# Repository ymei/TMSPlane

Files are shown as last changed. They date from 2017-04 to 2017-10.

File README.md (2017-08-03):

# Topmetal-S sensor tiled plane

## PCB

We use KiCad and python script to generate schematic, footprint, and PCB layout with minimal manual intervention.

### Procedure:
#### Schematic
1. Draw a Topmetal-S schematic symbol and save in a SCH library ```TMSch.lib```.  ```TMSch.lib``` is symlink-ed to every project.  When modifying the library, open the original ```.lib''' file directly instead of opening the symlinks.
2. run ```GenSch.py``` to generate desired schematic for the TMS array with correct net connectivity.  Here we save the generated file as ```array.sch```, which is a 2nd-level hierarchical schematic under ```Phi10cmBonding.sch```.
3. Open ```Phi10cmBonding.sch``` and generate a netlist.
#### PCB
1. Run ```KiPcbFp.py``` to generate a footprint ```TMS1mm.kicad_mod``` and save it under ```TMPcb.pretty``` which is a footprint library.  One may need to modify ```~/.config/kicad/fp-lib-table``` in order for KiCad to find the library: ```(lib (name Topmetal)(type KiCad)(uri ${KIPRJMOD}/TMPcb.pretty)(options "")(descr "Topmetal bonding footprints"))```.  An alternative is to save a local ```fp-lib-table``` file in the project directory.
2. Use pcbnew manually to setup a PCB `template' with appropriate layer structure, via and track classes etc.  Here we call the template ```template.kicad_pcb```.
3. Draw trace connections within a single footprint using a copy of the template PCB.  Save the single chip SCH and PCB as ```TMS1mm1chip.{sch,kicad_pcb}```.  It is preferable to place TMS1mm module's center at the very center in the unit cell.  It will be used as a reference (local origin).
4. Make a copy of the template PCB and load the netlist into it.  This step will bring all footprints into the PCB.
5. Run ```GenPcb.py``` which references the netlist-loaded PCB and ```TMS1mm1chip.pcb```, and generates the correctly laid out array.
6. **Remember to press `b' in pcbnew** to (re-)fill zones.

## Software
### KiCad

Pull source from https://github.com/KiCad/kicad-source-mirror and compile.

### KiCadScript in Hardware/PCB/KiCadScript/

#### Run scripts in Pcbnew's python shell:
```
import os, sys, runpy
scriptPath = os.environ['KIPRJMOD'] + "/../KiCadScript"
sys.path.append(scriptPath)
sys.argv = ['', '-h']
fileGlobals = runpy.run_path(scriptPath + "/GenSch2ExDAC.py", run_name="__main__")
```

#### Compile C source code to be used in python
```sh
cd KiAuto/hexlib/
python setup.py build
cd build
ln -s lib.freebsd-11.0-STABLE-amd64-2.7/hexlib.so .
```

### KiCad schematic sheets and netnames
KiCad schematic sheets are organized hierarchically.  Sheet paths are named as ```/58F9164E/58F91649``` with the numbers being timestamps in hex format.  Netnames local to a sheet start with a leading ```/```.  Global netnames do not have leading ```/```.

# PCB design and manufacturing

## Manufacturer capabilities

[Sunstone capabilities](http://www.sunstone.com/pcb-manufacturing-capabilities/detailed-capabilities)

|                     | Sunstone preferred | Sunstone capable |
| ------------------- |:------------------ |:---------------- |
| minimum drill size  | 0.008"             | 0.005"           |
| minimum trace width | 0.004" 1 oz Cu     | 0.003"           |
| trace clearance     | 0.004" 1 oz Cu     | 0.003"           |
| through-hole pad dia | 0.018" larger than finished hole dia | 0.016" larger |

Finished hole dia = drill dia - 4mil

### Typical board thickness in inch
```
0.062, 0.093, 0.125, 0.0886(14-layer), 0.0756 (16-layer)
```
1oz copper thickness is 34um (1.34mil)

### Typical drill sizes diameter in inch
```
0.008, 0.014, 0.020, 0.025, 0.029, 0.033, 0.035, 0.040, 0.043, 0.046, 0.052, 0.061,
0.067, 0.079, 0.088, 0.093, 0.100, 0.110, 0.125, 0.141, 0.150, 0.167, 0.192, 0.251
```
For boards thicker than 100mil, usually drill size cannot be smaller than board thickness / 10 (aspect ratio).

### Via
A recommendation: make the drill size diameter the same as the width of the trace, and the pad size roughly twice the diameter.

### Impedance
width/clearance 6mil/6mil and 4mil/4mil on surface layers, 4mil/7mil and 4mil/10mil inner layers are commonly used for Zo=50Ohm, Zdiff=100Ohm.

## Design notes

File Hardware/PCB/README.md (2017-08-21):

# TMS1mmX19 Carrier board (with TE0741 FPGA module)

1. Schematic done in KiCad, .asc netlist generated then imported into Mentor PADS for layout.  Remember to delete all **Nets** and modified/unwanted components in PADS before importing .asc.

## Features
1. TMS array power is logic (firmware/software) controlled via LDO EN pins.  Due to power-rail sharing, the relevant bias voltages and serial IO are also controlled by the switches.
2. All LDO design, no DC/DC.  For maximal efficiency, supply 4V power.  Maximum 5V allowed.
3. Serial IO, SDI, SDO, SCK, are multiplexed to drive one column (chain) at a time.  SDI and SCK have `high' as their idle states.

## Power requirement

### LTC2325-16 ADC
1. DVDD2V5 for OVdd: 31.5mA max
2. AVDD3V3 for Vdd : 44.5mA max

5 ADCs total, DVDD2V5: 157.5mA, AVDD3V3: 222.5mA

### LMK00105 for distributing CNVn to ADCs
1. DVDD2V5: 48mA

### 100MHz clock + CDCLVD1208 Clock distribution to ADCs
1. DVDD2V5: 25 + 75mA = 100mA

### 25MHz clock + CDCLVD1208 Clock distribution to SDMs
1. DVDD2V5: 90 + 75mA = 165mA

### ADR3412 + OPA350 for LVDS_VREF
1. DVDD2V5: 1 + 8.5mA = 10mA

DVDD2V5 requires total 545.5mA

# TMS1mmX19 19-chip array bonding board
## Signals and layers
### 16-layer stack-up, for 19-chip array TMS1mmX19.  Thickness 75.6mil, 1oz copper
1  F.Cu    Top copper layer
2  In1.Cu  AGND
3  In2.Cu  GND_NMOSI, DAC_BufferX2_VREF
4  In3.Cu  Gring, Ref3
5  In4.Cu  Ref2
6  In5.Cu  SDM_VDD_Shield, GND_VREF
7  In6.Cu  LVDS_VREF, Ref1
8  In7.Cu  AVDD
9  In8.Cu  AGND fill + RESET (as traces), SDM_testIN (as traces)
10 In9.Cu  DGND fill + slow digital signals: SDI, SDO, SCK
11 In10.Cu SDM_OUT1
12 In11.Cu DGND
13 In12.Cu CLK_P
14 In13.Cu CLK_N, SDM_OUT2
15 In14.Cu DVDD
16 B.Cu    Bottom copper layer

### 3.0mm-thick board produced by Edadoc
```
    Thickness(mil),   material,  DK
F.Cu 0.5oz+plating
    2.73 PP(1080 RC64)           3.81
In1.Cu  1oz
    5.12 CORE                    3.99
In2.Cu  1oz
    6.84 PP(1080 RC64+2116 RC57) 3.91
In3.Cu  1oz
    3.94 CORE                    4.12
In4.Cu  1oz
    5.04 PP(1080 RC64+1080 RC64) 3.81
In5.Cu  1oz
   18.11 CORE                    4.16
In6.Cu  1oz
    3.55 PP(106 RC76+106 RC76)   3.55
In7.Cu  1oz
    5.91 CORE                    4.25
In8.Cu  1oz
    4.01 PP(106 RC76+106 RC76)   3.55
In9.Cu  1oz
   18.11 CORE                    4.16
In10.Cu 1oz
    4.81 PP(1080 RC64+1080 RC64) 3.81
In11.Cu 1oz
    3.94 CORE                    4.12
In12.Cu 1oz
    6.30 PP(2116 RC57+1080 RC64) 3.91
In13.Cu 1oz
    5.12 CORE                    3.99
In14.Cu 1oz
    2.88 PP(1080 RC64)           3.81
B.Cu 0.5oz+plating
```

## FABRICATION NOTES
**All notes are applicable unless otherwise specified**

1. Materials: Green clad FR-4/Epoxy glass or equivalent.  Dielectric constant 4.2+/-0.2.  See cross-section drawing for board thickness, copper weight and layer structures.  RoHS compliant.
2. Components on top (front) and bottom (back) layers.
3. Minimum signal trace width/spacing: 4/4 mils.
4. Drilling.
  1. Minimum drill size is 8mil.
  2. All plated holes are to be plated through and with minimum copper thickness of 1mil.
  3. Drill sizes specified are actual drill sizes.  Finished hole sizes are expected to be 3~4mil smaller than the drill size.
  4. All PTH are to be within +/-3mil from true positions, NPTH to be within +/-2mil.
  5. See hole size table in the supplied NC drill file.
5. Layer-to-layer (pattern-to-pattern) registration (alignment) shall be within +/-5mil.
6. Soldermask: both sides of board, Liquid Photo Imageable, soldermask over bare copper (SMOBC), green.
7. Warpage and twist to meet IPC class II.  Shall not exceed 7mil per inch measured at any location or direction on the board.
8. Silkscreen shall use white non-conductive epoxy or equivalent.  Ink is NOT allowed on exposed plated area.
9. Finish.
  1. Edges to be free of loose silver and rough edge.
  2. Finished board shall not have nicks, scratches, voids, exposed copper, poor plating or mis-drilled holes.
  3. Trace width tolerance = +/-1mil of specified trace width.
  4. ENIG (Electroless nickel immersion gold) finish over copper.
10. Delivered boards shall be free of dirt, oil, finger prints and other contaminants.
11. Remove non-functional pad on all inner layers.
12. Manufacture's UL marking, flammability rating, logo and data code to be placed in silkscreen on bottom side of the board.
13. Impedance control
  1. All 19mil-wide traces on outer layers shall be 50Ohm single-ended +/-10%
  2. All 6mil/6mil width/spacing traces, including 4mil/4mil on outer layers and 4mil/7mil on inner layers shall be 100Ohm differential +/-10%

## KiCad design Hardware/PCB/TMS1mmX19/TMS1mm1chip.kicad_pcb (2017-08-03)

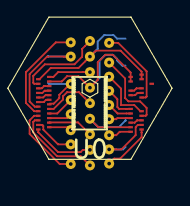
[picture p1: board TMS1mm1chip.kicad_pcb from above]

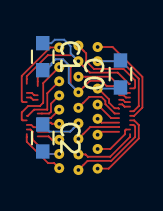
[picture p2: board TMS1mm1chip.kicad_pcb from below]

Board: 16 copper layers, 4 parts (3 on the bottom side), 12 nets.

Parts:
C0, C1, C2: 1u; C_0603
U0: TMS1mmAout1or2

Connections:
/AGND: C1.2, C2.2, U0.3, U0.28, U0.47, U0.49
/AVDD: C1.1, C2.1, U0.2, U0.27, U0.48, U0.50
/CSA_VBIASN_{}: U0.41, U0.42
/CSA_VBIASP_{}: U0.43, U0.44
/CSA_VDIS_{}: U0.7, U0.8
/CSA_VREF_{}: U0.5, U0.6
/DGND: C0.2, U0.14
/DVDD: C0.1, U0.13
/SDM_BIAS_{}: U0.29, U0.30
/SDO_{}: U0.24, U0.25
/VCASN_{}: U0.9, U0.10
/VCASP_{}: U0.11, U0.12

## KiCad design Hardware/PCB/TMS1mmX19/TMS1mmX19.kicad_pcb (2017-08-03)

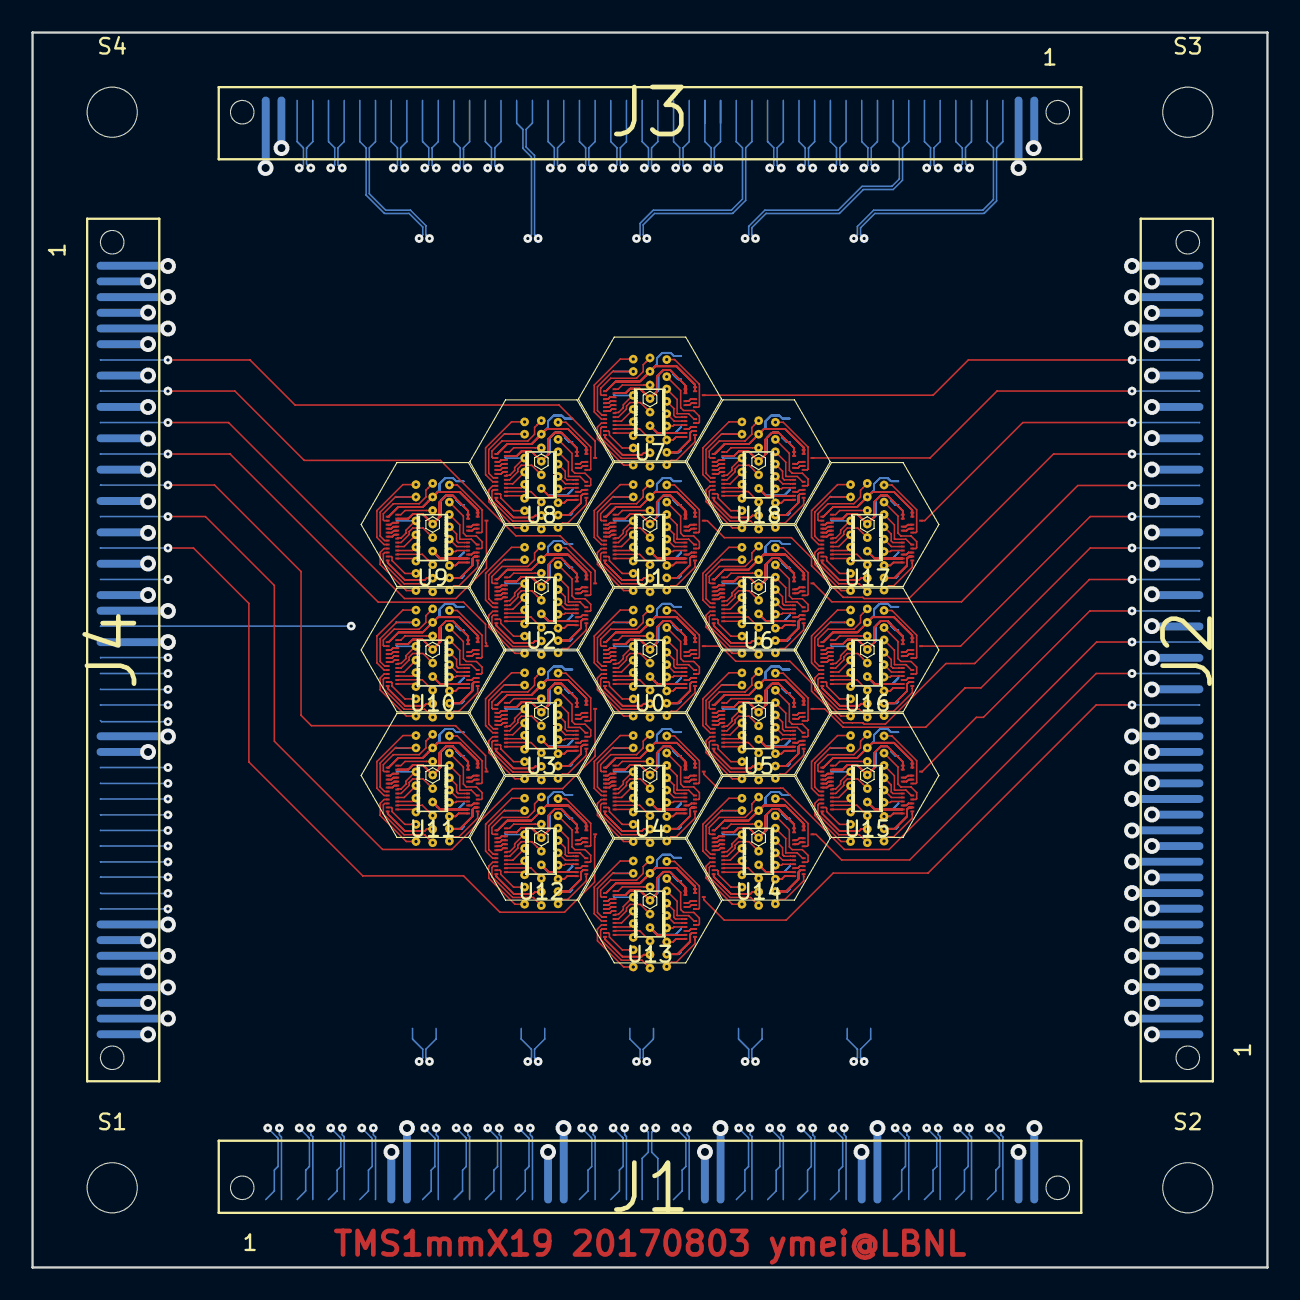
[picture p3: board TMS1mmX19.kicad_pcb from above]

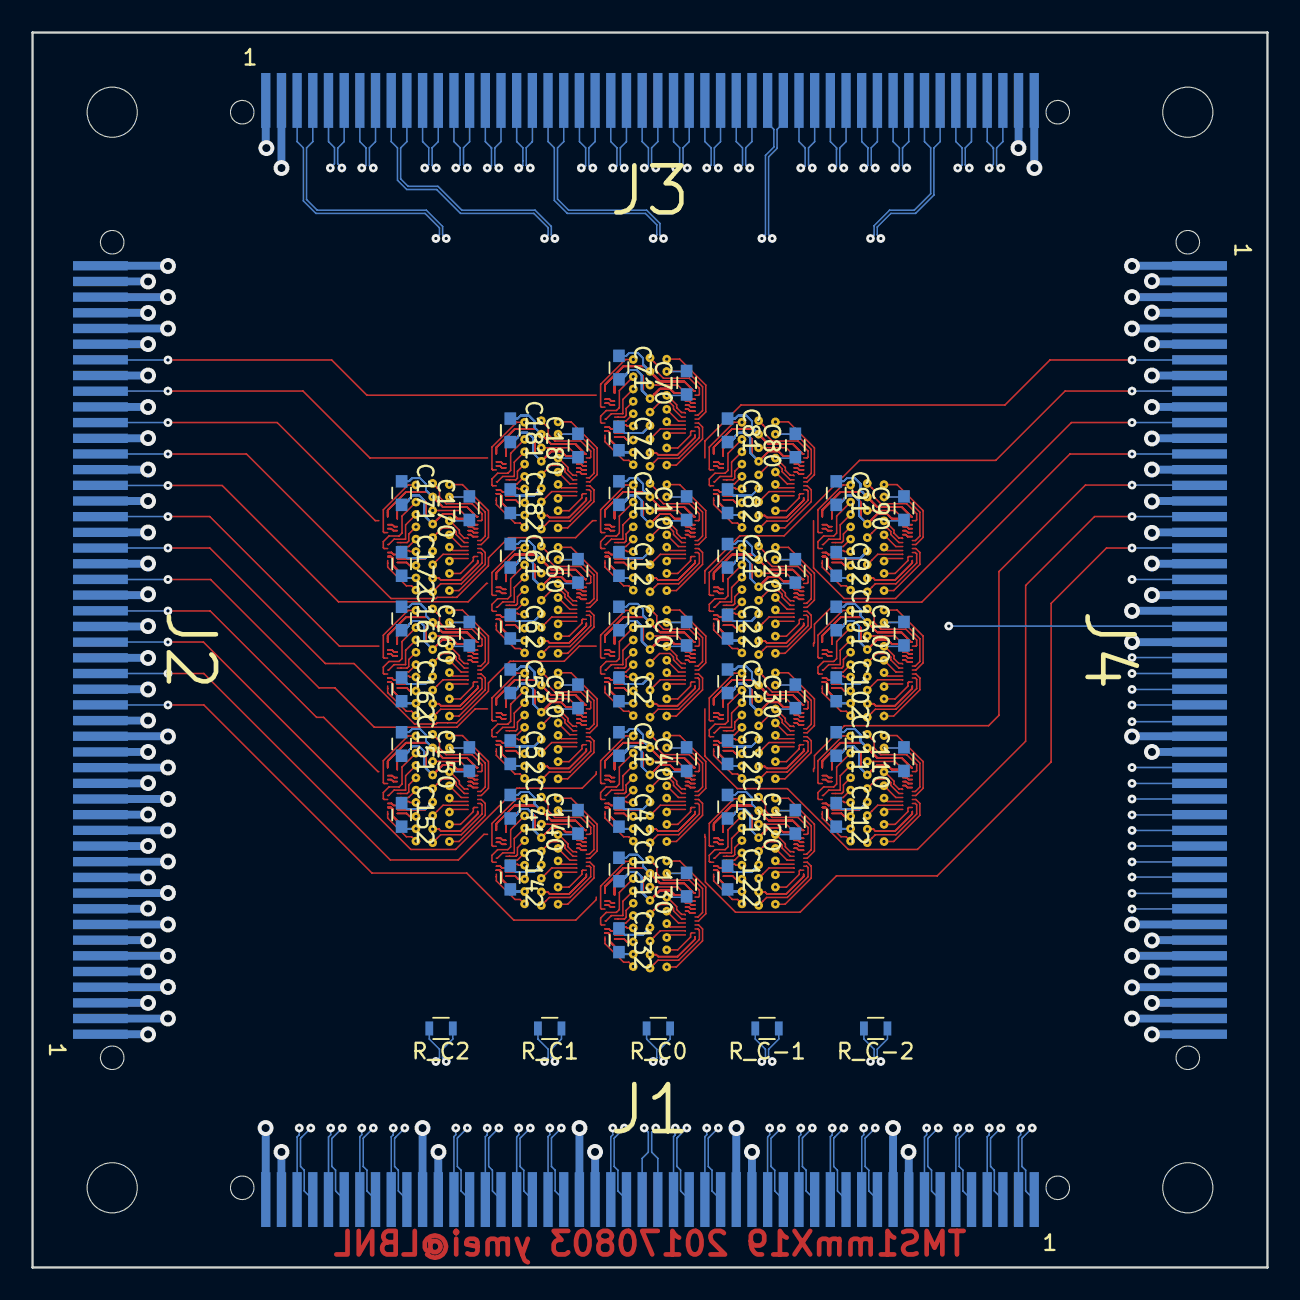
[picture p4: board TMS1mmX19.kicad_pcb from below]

Board: 16 copper layers, 78.7 x 78.7 mm, 89 parts (62 on the bottom side), 282 nets.

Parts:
C0, C1, C2, C10, C11, C12, C20, C21, C22, C30, C31, C32, C40, C41, C42, C50, C51, C52, C60, C61, C62, C70, C71, C72, C80, C81, C82, C90, C91, C92, C100, C101, C102, C110, C111, C112, C120, C121, C122, C130, C131, C132, C140, C141, C142, C150, C151, C152, C160, C161, C162, C170, C171, C172, C180, C181, C182: 1u; C_0603
J1, J2, J3, J4: FSI-150-XX-X-S-X-XX; FSI-150-XX-X-S-X-AD-recv-Bot
R_C0, R_C1, R_C2: 100; R_0603
R_C-1, R_C-2: 100; R_0603
S1, S2, S3, S4: Mounting Hole; MountingHole_3.2mm_M3
U0, U1, U2, U3, U4, U5, U6, U7, U8, U9, U10, U11, U12, U13, U14, U15, U16, U17, U18: TMS1mm; TMS1mmAout1or2

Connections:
AGND: C1.2, C2.2, C11.2, C12.2, C21.2, C22.2, C31.2, C32.2, C41.2, C42.2, C51.2, C52.2, C61.2, C62.2, C71.2, C72.2, C81.2, C82.2, C91.2, C92.2, C101.2, C102.2, C111.2, C112.2, C121.2, C122.2, C131.2, C132.2, C141.2, C142.2, C151.2, C152.2, C161.2, C162.2, C171.2, C172.2, C181.2, C182.2, J2.5, J2.6, J2.13, J2.14, J2.15, J2.16, J2.17, J2.18, J2.19, J2.20, J2.21, J2.23, J2.25, J2.27, J2.29, J2.31, J2.33, J2.35, J2.37, J2.39, J2.41, J2.43, J4.5, J4.6, J4.8, J4.10, J4.12, J4.14, J4.16, J4.18, J4.20, J4.22, J4.23, J4.25, U0.3, U0.28, U0.47, U0.49, U1.3, U1.28, U1.47, U1.49, U2.3, U2.28, U2.47, U2.49, U3.3, U3.28, U3.47, U3.49, U4.3, U4.28, U4.47, U4.49, U5.3, U5.28, U5.47, U5.49, U6.3, U6.28, U6.47, U6.49, U7.3, U7.28, U7.47, U7.49, U8.3, U8.28, U8.47, U8.49, U9.3, U9.28, U9.47, U9.49, U10.3, U10.28, U10.47, U10.49, U11.3, U11.28, U11.47, U11.49, U12.3, U12.28, U12.47, U12.49, U13.3, U13.28, U13.47, U13.49, U14.3, U14.28, U14.47, U14.49, U15.3, U15.28, U15.47, U15.49, U16.3, U16.28, U16.47, U16.49, U17.3, U17.28, U17.47, U17.49, U18.3, U18.28, U18.47, U18.49
AOUT1_CSA_0: J2.32, U0.46
AOUT1_CSA_1: J2.38, U1.46
AOUT1_CSA_2: J4.9, U2.46
AOUT1_CSA_3: J4.17, U3.46
AOUT1_CSA_4: J2.26, U4.46
AOUT1_CSA_5: J2.30, U5.46
AOUT1_CSA_6: J2.36, U6.46
AOUT1_CSA_7: J2.44, U7.46
AOUT1_CSA_8: J4.7, U8.46
AOUT1_CSA_9: J4.11, U9.46
AOUT1_CSA_10: J4.13, U10.46
AOUT1_CSA_11: J4.15, U11.46
AOUT1_CSA_12: J4.19, U12.46
AOUT1_CSA_13: J2.22, U13.46
AOUT1_CSA_14: J2.24, U14.46
AOUT1_CSA_15: J2.28, U15.46
AOUT1_CSA_16: J2.34, U16.46
AOUT1_CSA_17: J2.40, U17.46
AOUT1_CSA_18: J2.42, U18.46
AVDD: C1.1, C2.1, C11.1, C12.1, C21.1, C22.1, C31.1, C32.1, C41.1, C42.1, C51.1, C52.1, C61.1, C62.1, C71.1, C72.1, C81.1, C82.1, C91.1, C92.1, C101.1, C102.1, C111.1, C112.1, C121.1, C122.1, C131.1, C132.1, C141.1, C142.1, C151.1, C152.1, C161.1, C162.1, C171.1, C172.1, C181.1, C182.1, J2.9, J2.10, J2.11, J2.12, J2.45, J2.46, J4.43, J4.44, J4.45, J4.46, U0.2, U0.27, U0.48, U0.50, U1.2, U1.27, U1.48, U1.50, U2.2, U2.27, U2.48, U2.50, U3.2, U3.27, U3.48, U3.50, U4.2, U4.27, U4.48, U4.50, U5.2, U5.27, U5.48, U5.50, U6.2, U6.27, U6.48, U6.50, U7.2, U7.27, U7.48, U7.50, U8.2, U8.27, U8.48, U8.50, U9.2, U9.27, U9.48, U9.50, U10.2, U10.27, U10.48, U10.50, U11.2, U11.27, U11.48, U11.50, U12.2, U12.27, U12.48, U12.50, U13.2, U13.27, U13.48, U13.50, U14.2, U14.27, U14.48, U14.50, U15.2, U15.27, U15.48, U15.50, U16.2, U16.27, U16.48, U16.50, U17.2, U17.27, U17.48, U17.50, U18.2, U18.27, U18.48, U18.50
CLK_0_N: J3.20, R_C0.2, U0.21, U1.21, U4.21, U7.21, U13.21
CLK_0_P: J3.19, R_C0.1, U0.22, U1.22, U4.22, U7.22, U13.22
CLK_1_N: J3.10, R_C1.2, U5.21, U6.21, U14.21, U18.21
CLK_1_P: J3.9, R_C1.1, U5.22, U6.22, U14.22, U18.22
CLK_2_N: J3.4, R_C2.2, U15.21, U16.21, U17.21
CLK_2_P: J3.3, R_C2.1, U15.22, U16.22, U17.22
CLK_-1_N: J3.34, R_C-1.2, U2.21, U3.21, U8.21, U12.21
CLK_-1_P: J3.33, R_C-1.1, U2.22, U3.22, U8.22, U12.22
CLK_-2_N: J3.44, R_C-2.2, U9.21, U10.21, U11.21
CLK_-2_P: J3.43, R_C-2.1, U9.22, U10.22, U11.22
CSA_VBIASN_0: U0.41, U0.42
CSA_VBIASN_1: U1.41, U1.42
CSA_VBIASN_2: U2.41, U2.42
CSA_VBIASN_3: U3.41, U3.42
CSA_VBIASN_4: U4.41, U4.42
CSA_VBIASN_5: U5.41, U5.42
CSA_VBIASN_6: U6.41, U6.42
CSA_VBIASN_7: U7.41, U7.42
CSA_VBIASN_8: U8.41, U8.42
CSA_VBIASN_9: U9.41, U9.42
CSA_VBIASN_10: U10.41, U10.42
CSA_VBIASN_11: U11.41, U11.42
CSA_VBIASN_12: U12.41, U12.42
CSA_VBIASN_13: U13.41, U13.42
CSA_VBIASN_14: U14.41, U14.42
CSA_VBIASN_15: U15.41, U15.42
CSA_VBIASN_16: U16.41, U16.42
CSA_VBIASN_17: U17.41, U17.42
CSA_VBIASN_18: U18.41, U18.42
CSA_VBIASP_0: U0.43, U0.44
CSA_VBIASP_1: U1.43, U1.44
CSA_VBIASP_2: U2.43, U2.44
CSA_VBIASP_3: U3.43, U3.44
CSA_VBIASP_4: U4.43, U4.44
CSA_VBIASP_5: U5.43, U5.44
CSA_VBIASP_6: U6.43, U6.44
CSA_VBIASP_7: U7.43, U7.44
CSA_VBIASP_8: U8.43, U8.44
CSA_VBIASP_9: U9.43, U9.44
CSA_VBIASP_10: U10.43, U10.44
CSA_VBIASP_11: U11.43, U11.44
CSA_VBIASP_12: U12.43, U12.44
CSA_VBIASP_13: U13.43, U13.44
CSA_VBIASP_14: U14.43, U14.44
CSA_VBIASP_15: U15.43, U15.44
CSA_VBIASP_16: U16.43, U16.44
CSA_VBIASP_17: U17.43, U17.44
CSA_VBIASP_18: U18.43, U18.44
CSA_VDIS_0: U0.7, U0.8
CSA_VDIS_1: U1.7, U1.8
CSA_VDIS_2: U2.7, U2.8
CSA_VDIS_3: U3.7, U3.8
CSA_VDIS_4: U4.7, U4.8
CSA_VDIS_5: U5.7, U5.8
CSA_VDIS_6: U6.7, U6.8
CSA_VDIS_7: U7.7, U7.8
CSA_VDIS_8: U8.7, U8.8
CSA_VDIS_9: U9.7, U9.8
CSA_VDIS_10: U10.7, U10.8
CSA_VDIS_11: U11.7, U11.8
CSA_VDIS_12: U12.7, U12.8
CSA_VDIS_13: U13.7, U13.8
CSA_VDIS_14: U14.7, U14.8
CSA_VDIS_15: U15.7, U15.8
CSA_VDIS_16: U16.7, U16.8
CSA_VDIS_17: U17.7, U17.8
CSA_VDIS_18: U18.7, U18.8
CSA_VREF_0: U0.5, U0.6
CSA_VREF_1: U1.5, U1.6
CSA_VREF_2: U2.5, U2.6
CSA_VREF_3: U3.5, U3.6
CSA_VREF_4: U4.5, U4.6
CSA_VREF_5: U5.5, U5.6
CSA_VREF_6: U6.5, U6.6
CSA_VREF_7: U7.5, U7.6
CSA_VREF_8: U8.5, U8.6
CSA_VREF_9: U9.5, U9.6
CSA_VREF_10: U10.5, U10.6
CSA_VREF_11: U11.5, U11.6
CSA_VREF_12: U12.5, U12.6
CSA_VREF_13: U13.5, U13.6
CSA_VREF_14: U14.5, U14.6
CSA_VREF_15: U15.5, U15.6
CSA_VREF_16: U16.5, U16.6
CSA_VREF_17: U17.5, U17.6
CSA_VREF_18: U18.5, U18.6
DAC_BufferX2_VREF: J4.47, J4.48, U0.40, U1.40, U2.40, U3.40, U4.40, U5.40, U6.40, U7.40, U8.40, U9.40, U10.40, U11.40, U12.40, U13.40, U14.40, U15.40, U16.40, U17.40, U18.40
DGND: C0.2, C10.2, C20.2, C30.2, C40.2, C50.2, C60.2, C70.2, C80.2, C90.2, C100.2, C110.2, C120.2, C130.2, C140.2, C150.2, C160.2, C170.2, C180.2, J1.9, J1.10, J1.19, J1.20, J1.29, J1.30, J3.49, J3.50, J4.31, J4.32, U0.14, U1.14, U2.14, U3.14, U4.14, U5.14, U6.14, U7.14, U8.14, U9.14, U10.14, U11.14, U12.14, U13.14, U14.14, U15.14, U16.14, U17.14, U18.14
DVDD: C0.1, C10.1, C20.1, C30.1, C40.1, C50.1, C60.1, C70.1, C80.1, C90.1, C100.1, C110.1, C120.1, C130.1, C140.1, C150.1, C160.1, C170.1, C180.1, J1.39, J1.40, J1.49, J1.50, J3.1, J3.2, U0.13, U1.13, U2.13, U3.13, U4.13, U5.13, U6.13, U7.13, U8.13, U9.13, U10.13, U11.13, U12.13, U13.13, U14.13, U15.13, U16.13, U17.13, U18.13
GND_NMOSI: J4.3, J4.4, U0.4, U1.4, U2.4, U3.4, U4.4, U5.4, U6.4, U7.4, U8.4, U9.4, U10.4, U11.4, U12.4, U13.4, U14.4, U15.4, U16.4, U17.4, U18.4
GND_VREF: J2.3, J2.4, U0.31, U1.31, U2.31, U3.31, U4.31, U5.31, U6.31, U7.31, U8.31, U9.31, U10.31, U11.31, U12.31, U13.31, U14.31, U15.31, U16.31, U17.31, U18.31
Gring: J4.1, J4.2, U0.1, U1.1, U2.1, U3.1, U4.1, U5.1, U6.1, U7.1, U8.1, U9.1, U10.1, U11.1, U12.1, U13.1, U14.1, U15.1, U16.1, U17.1, U18.1
LVDS_VREF: J2.49, J2.50, U0.15, U1.15, U2.15, U3.15, U4.15, U5.15, U6.15, U7.15, U8.15, U9.15, U10.15, U11.15, U12.15, U13.15, U14.15, U15.15, U16.15, U17.15, U18.15
RESET: J4.24, U0.16, U1.16, U2.16, U3.16, U4.16, U5.16, U6.16, U7.16, U8.16, U9.16, U10.16, U11.16, U12.16, U13.16, U14.16, U15.16, U16.16, U17.16, U18.16
Ref1: J2.1, J2.2, U0.33, U1.33, U2.33, U3.33, U4.33, U5.33, U6.33, U7.33, U8.33, U9.33, U10.33, U11.33, U12.33, U13.33, U14.33, U15.33, U16.33, U17.33, U18.33
Ref2: J2.7, J2.8, U0.34, U1.34, U2.34, U3.34, U4.34, U5.34, U6.34, U7.34, U8.34, U9.34, U10.34, U11.34, U12.34, U13.34, U14.34, U15.34, U16.34, U17.34, U18.34
Ref3: J4.49, J4.50, U0.32, U1.32, U2.32, U3.32, U4.32, U5.32, U6.32, U7.32, U8.32, U9.32, U10.32, U11.32, U12.32, U13.32, U14.32, U15.32, U16.32, U17.32, U18.32
SCK_0: J4.37, U0.23, U1.23, U4.23, U7.23, U13.23
SCK_1: J4.39, U5.23, U6.23, U14.23, U18.23
SCK_2: J4.41, U15.23, U16.23, U17.23
SCK_-1: J4.35, U2.23, U3.23, U8.23, U12.23
SCK_-2: J4.33, U9.23, U10.23, U11.23
SDM_BIAS_0: U0.29, U0.30
SDM_BIAS_1: U1.29, U1.30
SDM_BIAS_2: U2.29, U2.30
SDM_BIAS_3: U3.29, U3.30
SDM_BIAS_4: U4.29, U4.30
SDM_BIAS_5: U5.29, U5.30
SDM_BIAS_6: U6.29, U6.30
SDM_BIAS_7: U7.29, U7.30
SDM_BIAS_8: U8.29, U8.30
SDM_BIAS_9: U9.29, U9.30
SDM_BIAS_10: U10.29, U10.30
SDM_BIAS_11: U11.29, U11.30
SDM_BIAS_12: U12.29, U12.30
SDM_BIAS_13: U13.29, U13.30
SDM_BIAS_14: U14.29, U14.30
SDM_BIAS_15: U15.29, U15.30
SDM_BIAS_16: U16.29, U16.30
SDM_BIAS_17: U17.29, U17.30
SDM_BIAS_18: U18.29, U18.30
SDM_OUT1_0_N: J3.31, U0.19
SDM_OUT1_0_P: J3.32, U0.20
SDM_OUT1_1_N: J3.27, U1.19
SDM_OUT1_1_P: J3.28, U1.20
SDM_OUT1_2_N: J3.41, U2.19
SDM_OUT1_2_P: J3.42, U2.20
SDM_OUT1_3_N: J1.11, U3.19
SDM_OUT1_3_P: J1.12, U3.20
SDM_OUT1_4_N: J1.21, U4.19
SDM_OUT1_4_P: J1.22, U4.20
SDM_OUT1_5_N: J1.31, U5.19
SDM_OUT1_5_P: J1.32, U5.20
SDM_OUT1_6_N: J3.17, U6.19
SDM_OUT1_6_P: J3.18, U6.20
SDM_OUT1_7_N: J3.23, U7.19
SDM_OUT1_7_P: J3.24, U7.20
SDM_OUT1_8_N: J3.37, U8.19
SDM_OUT1_8_P: J3.38, U8.20
SDM_OUT1_9_N: J3.47, U9.19
SDM_OUT1_9_P: J3.48, U9.20
SDM_OUT1_10_N: J1.1, U10.19
SDM_OUT1_10_P: J1.2, U10.20
SDM_OUT1_11_N: J1.5, U11.19
SDM_OUT1_11_P: J1.6, U11.20
SDM_OUT1_12_N: J1.15, U12.19
SDM_OUT1_12_P: J1.16, U12.20
SDM_OUT1_13_N: J1.25, U13.19
SDM_OUT1_13_P: J1.26, U13.20
SDM_OUT1_14_N: J1.35, U14.19
SDM_OUT1_14_P: J1.36, U14.20
SDM_OUT1_15_N: J1.45, U15.19
SDM_OUT1_15_P: J1.46, U15.20
SDM_OUT1_16_N: J1.41, U16.19
SDM_OUT1_16_P: J1.42, U16.20
SDM_OUT1_17_N: J3.7, U17.19
SDM_OUT1_17_P: J3.8, U17.20
SDM_OUT1_18_N: J3.13, U18.19
SDM_OUT1_18_P: J3.14, U18.20
SDM_OUT2_0_N: J3.30, U0.18
SDM_OUT2_0_P: J3.29, U0.17
SDM_OUT2_1_N: J3.26, U1.18
SDM_OUT2_1_P: J3.25, U1.17
SDM_OUT2_2_N: J3.40, U2.18
SDM_OUT2_2_P: J3.39, U2.17
SDM_OUT2_3_N: J1.14, U3.18
SDM_OUT2_3_P: J1.13, U3.17
SDM_OUT2_4_N: J1.24, U4.18
SDM_OUT2_4_P: J1.23, U4.17
SDM_OUT2_5_N: J1.34, U5.18
SDM_OUT2_5_P: J1.33, U5.17
SDM_OUT2_6_N: J3.16, U6.18
SDM_OUT2_6_P: J3.15, U6.17
SDM_OUT2_7_N: J3.22, U7.18
SDM_OUT2_7_P: J3.21, U7.17
SDM_OUT2_8_N: J3.36, U8.18
SDM_OUT2_8_P: J3.35, U8.17
SDM_OUT2_9_N: J3.46, U9.18
SDM_OUT2_9_P: J3.45, U9.17
SDM_OUT2_10_N: J1.4, U10.18
SDM_OUT2_10_P: J1.3, U10.17
SDM_OUT2_11_N: J1.8, U11.18
SDM_OUT2_11_P: J1.7, U11.17
SDM_OUT2_12_N: J1.18, U12.18
SDM_OUT2_12_P: J1.17, U12.17
SDM_OUT2_13_N: J1.28, U13.18
SDM_OUT2_13_P: J1.27, U13.17
SDM_OUT2_14_N: J1.38, U14.18
SDM_OUT2_14_P: J1.37, U14.17
SDM_OUT2_15_N: J1.48, U15.18
SDM_OUT2_15_P: J1.47, U15.17
SDM_OUT2_16_N: J1.44, U16.18
SDM_OUT2_16_P: J1.43, U16.17
SDM_OUT2_17_N: J3.6, U17.18
SDM_OUT2_17_P: J3.5, U17.17
SDM_OUT2_18_N: J3.12, U18.18
SDM_OUT2_18_P: J3.11, U18.17
SDM_VDD_Shield: J2.47, J2.48, U0.26, U1.26, U2.26, U3.26, U4.26, U5.26, U6.26, U7.26, U8.26, U9.26, U10.26, U11.26, U12.26, U13.26, U14.26, U15.26, U16.26, U17.26, U18.26
SDM_testIN: J4.21, U0.35, U1.35, U2.35, U3.35, U4.35, U5.35, U6.35, U7.35, U8.35, U9.35, U10.35, U11.35, U12.35, U13.35, U14.35, U15.35, U16.35, U17.35, U18.35
SDO_0: U0.25, U1.24
SDO_1: U1.25, U7.24
SDO_2: U2.25, U8.24
SDO_3: U2.24, U3.25
SDO_4: U0.24, U4.25
SDO_5: U5.25, U6.24
SDO_6: U6.25, U18.24
SDO_7: J4.28, U7.25
SDO_8: J4.29, U8.25
SDO_9: J4.30, U9.25
SDO_10: U9.24, U10.25
SDO_11: U10.24, U11.25
SDO_12: U3.24, U12.25
SDO_13: U4.24, U13.25
SDO_14: U5.24, U14.25
SDO_15: U15.25, U16.24
SDO_16: U16.25, U17.24
SDO_17: J4.26, U17.25
SDO_18: J4.27, U18.25
SDO_26: J4.34, U11.24
SDO_27: J4.36, U12.24
SDO_28: J4.38, U13.24
SDO_29: J4.40, U14.24
SDO_30: J4.42, U15.24
VCASN_0: U0.9, U0.10
VCASN_1: U1.9, U1.10
VCASN_2: U2.9, U2.10
VCASN_3: U3.9, U3.10
VCASN_4: U4.9, U4.10
VCASN_5: U5.9, U5.10
VCASN_6: U6.9, U6.10
VCASN_7: U7.9, U7.10
VCASN_8: U8.9, U8.10
VCASN_9: U9.9, U9.10
VCASN_10: U10.9, U10.10
VCASN_11: U11.9, U11.10
VCASN_12: U12.9, U12.10
VCASN_13: U13.9, U13.10
VCASN_14: U14.9, U14.10
VCASN_15: U15.9, U15.10
VCASN_16: U16.9, U16.10
VCASN_17: U17.9, U17.10
VCASN_18: U18.9, U18.10
VCASP_0: U0.11, U0.12
VCASP_1: U1.11, U1.12
VCASP_2: U2.11, U2.12
VCASP_3: U3.11, U3.12
VCASP_4: U4.11, U4.12
VCASP_5: U5.11, U5.12
VCASP_6: U6.11, U6.12
VCASP_7: U7.11, U7.12
VCASP_8: U8.11, U8.12
VCASP_9: U9.11, U9.12
VCASP_10: U10.11, U10.12
VCASP_11: U11.11, U11.12
VCASP_12: U12.11, U12.12
VCASP_13: U13.11, U13.12
VCASP_14: U14.11, U14.12
VCASP_15: U15.11, U15.12
VCASP_16: U16.11, U16.12
VCASP_17: U17.11, U17.12
VCASP_18: U18.11, U18.12

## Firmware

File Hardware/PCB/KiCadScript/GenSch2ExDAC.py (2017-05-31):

#!/usr/bin/env python

## \file
# Generate schematic of Topmetal-S array using 2 external DACs per sensor.
#
# usage: GenSch2ExDAC.py [-h] [-n NCHIPS] [-p PITCH] ofn
#
# positional arguments:
#   ofn                   Output file [.sch]
#
# optional arguments:
#   -h, --help            show this help message and exit
#   -n NCHIPS, --nchips NCHIPS
#                         Number of chips to place [127]
#   -p PITCH, --pitch PITCH
#                         Pitch between chip symbols [4000]
#

from __future__ import print_function

import sys
import argparse

from KiAuto import *
from KiAuto.HexLib import *

TMS1mmNetTemplate = {
    1 : "Gring",
    2 : "AVDD",
    3 : "AGND",
    4 : "GND_NMOSI",
    5 : "CSA_VREF_{}", # DAC6
    6 : "CSA_VREF_{}",
    7 : "CSA_VDIS_{}", # DAC5
    8 : "CSA_VDIS_{}",
    9 : "VCASN_{}",    # DAC3
    10 : "VCASN_{}",
    11 : "VCASP_{}",   # DAC4
    12 : "VCASP_{}",
    13 : "DVDD",
    14 : "DGND",
    15 : "LVDS_VREF",
    16 : "RESET",
    17 : "SDM_OUT2_{}_P",
    18 : "SDM_OUT2_{}_N",
    19 : "SDM_OUT1_{}_N",
    20 : "SDM_OUT1_{}_P",
    21 : "CLK_{}_N",
    22 : "CLK_{}_P",
    23 : "SCK_{}",
    24 : "SDO_{}", # this sensor's SDI fed by another chip's SDO
    25 : "SDO_{}",
    26 : "SDM_VDD_Shield",
    27 : "AVDD",
    28 : "AGND",
    29 : "SDM_BIAS_{}", # IN
    30 : "SDM_BIAS_{}", # OUT
    31 : "GND_VREF",
    32 : "Ref3",
    33 : "Ref1",
    34 : "Ref2",
    35 : "SDM_testIN",
    36 : "", # AOUT3N_CSA
    37 : "", # AOUT3P_CSA
    38 : "", # AOUT_BufferX2
    39 : "", # BufferX2_testIN
    40 : "DAC_BufferX2_VREF",
    41 : "CSA_VBIASN_{}",
    42 : "CSA_VBIASN_{}", # DAC1
    43 : "CSA_VBIASP_{}",
    44 : "CSA_VBIASP_{}", # DAC2
    45 : "", # AOUT2_CSA
    46 : "AOUT1_CSA_{}",
    47 : "AGND",
    48 : "AVDD",
    49 : "AGND",
    50 : "AVDD"
}

def get_labels(id, template):
    hex = Hex()
    labels = []
    qr = hex.l2qr(id)
    l = hex.qr2l((qr[0], qr[1]-1))
    for i in xrange(len(template)):
        v = template[i+1]
        if 'SCK_{}' in v or 'CLK_{}' in v:
            labels.append(v.format(qr[0]))
        elif i+1 == 24:
            labels.append(v.format(l))
        elif '{}' in v:
            labels.append(v.format(id))
        else:
            labels.append(v)
    return labels

if __name__ == "__main__":

    parser = argparse.ArgumentParser()
    parser.add_argument("-n", "--nchips", type=int, default=127,
                        help="Number of chips to place [127]")
    parser.add_argument("-p", "--pitch", type=int, default=4000,
                        help="Pitch between chip symbols [4000]")
    parser.add_argument("-l", "--ltype", type=str, default="G", choices=["L", "H", "G"],
                        help="Label type, L (local), H, or G (global) [G]")
    parser.add_argument("ofn", type=str, default="out.sch",
                        help="Output file [.sch]")
    args = parser.parse_args()

    hex = Hex()
    # print(TMS1mmNetTemplate[5].format(5))

    sch = KiSch()
    sheetid = 1
    sheettot = 1
    if args.ltype != "L":
        sheetid = 2
        sheettot = 3
    sch.set_descr(paper="User 20000 22000", sheetid=sheetid, sheettot=sheettot,
                  title="Topmetal-S array")
    sch.add_to_libs("LIBS:TMSch\n")
    comps = ""
    schCenter = (10000, 11000)
    cnYoff = 1650
    cnXp = 500

    for i in xrange(args.nchips):
        qr = hex.l2qr(i)
        xy = hex.qr2xy(args.pitch, qr)

        loc = (int(xy[0])+schCenter[0], schCenter[1]-int(xy[1]))
        labels = get_labels(i, TMS1mmNetTemplate)
        Un = KiSchCompTMS1mm("U{}".format(i), loc, val="TMS1mm", fp="Topmetal:TMS1mm2ExDAC",
                             labels=labels, ltype=args.ltype)
        comps += str(Un)
        Cn = []
        Ln = []
        for j in xrange(3):
            cloc = (loc[0]-cnXp+j*cnXp, loc[1]+cnYoff)
            Cn.append(KiSchCompC("C{}".format(i*10+j), cloc, val="1u", fp="Capacitors_SMD:C_0603"))
            if j == 0:
                Ln.append(KiSchLabel("DGND", (cloc[0], cloc[1]+150), ltype=args.ltype))
                Ln.append(KiSchLabel("DVDD", (cloc[0], cloc[1]-150), ltype=args.ltype))
            else:
                Ln.append(KiSchLabel("AGND", (cloc[0], cloc[1]+150), ltype=args.ltype))
                Ln.append(KiSchLabel("AVDD", (cloc[0], cloc[1]-150), ltype=args.ltype))
        for Ci in Cn:
            comps += str(Ci)
        for Li in Ln:
            comps += str(Li)

    sch.set_content(comps)
    with open(args.ofn, "w") as ofile:
        ofile.write(str(sch))

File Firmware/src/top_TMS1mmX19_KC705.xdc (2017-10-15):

# KC705 configuration
set_property CFGBVS VCCO [current_design]
set_property CONFIG_VOLTAGE 2.5 [current_design]
# enable if ENABLE_TEN_GIG_ETH = false
set_property BITSTREAM.General.UnconstrainedPins {Allow} [current_design]

# 200MHz onboard diff clock
create_clock -name system_clock -period 5.0 [get_ports {SYS_CLK_P}]
# 156.25MHz
create_clock -name user_clock   -period 6.4 [get_ports {USER_CLK_P}]
create_clock -name si5324_clock -period 6.4 [get_ports {SI5324CLK_P}]
# 125MHz
create_clock -name sgmii_clock  -period 8.0 [get_ports {SGMIICLK_Q0_P}]

# PadFunction: IO_L12P_T1_MRCC_33
set_property -dict {PACKAGE_PIN AD12 IOSTANDARD DIFF_SSTL15 VCCAUX_IO DONTCARE} [get_ports {SYS_CLK_P}]
# PadFunction: IO_L12N_T1_MRCC_33
set_property -dict {PACKAGE_PIN AD11 IOSTANDARD DIFF_SSTL15 VCCAUX_IO DONTCARE} [get_ports {SYS_CLK_N}]

# Set DCI_CASCADE
set_property slave_banks {32 34} [get_iobanks 33]

# 156.25MHz clock, IOSTANDARD is overridden in IBUFDS
set_property -dict {PACKAGE_PIN K28 IOSTANDARD LVDS_25} [get_ports {USER_CLK_P}]
set_property -dict {PACKAGE_PIN K29 IOSTANDARD LVDS_25} [get_ports {USER_CLK_N}]

# 125MHz clock, for GTP/GTH/GTX
set_property PACKAGE_PIN G8 [get_ports {SGMIICLK_Q0_P}]
set_property PACKAGE_PIN G7 [get_ports {SGMIICLK_Q0_N}]

# External clock IC Si5324
set_property -dict {PACKAGE_PIN AE20 IOSTANDARD LVCMOS25} [get_ports SI5324_RSTn]
set_property PACKAGE_PIN L8 [get_ports SI5324CLK_P]
set_property PACKAGE_PIN L7 [get_ports SI5324CLK_N]

# clock domain interaction, must explictly specify all possible pairs.
# Command with only one `-group' parameter means the clock is asynchronous to all other, including generated from its own, clocks.
set_clock_groups -asynchronous -group [get_clocks -include_generated_clocks system_clock] -group [get_clocks -include_generated_clocks user_clock]
set_clock_groups -asynchronous -group [get_clocks -include_generated_clocks system_clock] -group [get_clocks -include_generated_clocks si5324_clock]
set_clock_groups -asynchronous -group [get_clocks -include_generated_clocks system_clock] -group [get_clocks -include_generated_clocks sgmii_clock]
set_clock_groups -asynchronous -group [get_clocks -include_generated_clocks user_clock]   -group [get_clocks -include_generated_clocks si5324_clock]
set_clock_groups -asynchronous -group [get_clocks -include_generated_clocks user_clock]   -group [get_clocks -include_generated_clocks sgmii_clock]
set_clock_groups -asynchronous -group [get_clocks -include_generated_clocks si5324_clock] -group [get_clocks -include_generated_clocks sgmii_clock]

# seems we ran out of bufg's
# set_property CLOCK_DEDICATED_ROUTE BACKBONE [get_nets global_clock_reset_inst/I]
# false path of resetter
set_false_path -from [get_pins -of_objects [get_cells -hierarchical -filter {NAME =~ *GLOBAL_RST_reg*}] -filter {NAME =~ *C}]

#<-- LEDs, buttons and switches --<

# Bank: 33 - GPIO_SW_7 (CPU_RESET)
set_property -dict {PACKAGE_PIN AB7 IOSTANDARD LVCMOS15 VCCAUX_IO DONTCARE SLEW SLOW} [get_ports {SYS_RST}]
# LED:
# Bank: 33 - GPIO_LED_0_LS
set_property -dict {PACKAGE_PIN AB8 IOSTANDARD LVCMOS15 DRIVE 12 SLEW SLOW} [get_ports {LED8Bit[0]}]
# Bank: 33 - GPIO_LED_1_LS
set_property -dict {PACKAGE_PIN AA8 IOSTANDARD LVCMOS15 DRIVE 12 SLEW SLOW} [get_ports {LED8Bit[1]}]
# Bank: 33 - GPIO_LED_2_LS
set_property -dict {PACKAGE_PIN AC9 IOSTANDARD LVCMOS15 DRIVE 12 SLEW SLOW} [get_ports {LED8Bit[2]}]
# Bank: 33 - GPIO_LED_3_LS
set_property -dict {PACKAGE_PIN AB9 IOSTANDARD LVCMOS15 DRIVE 12 SLEW SLOW} [get_ports {LED8Bit[3]}]
# Bank: - GPIO_LED_4_LS
set_property -dict {PACKAGE_PIN AE26 IOSTANDARD LVCMOS25 DRIVE 12 SLEW SLOW} [get_ports {LED8Bit[4]}]
# Bank: - GPIO_LED_5_LS
set_property -dict {PACKAGE_PIN G19 IOSTANDARD LVCMOS25 DRIVE 12 SLEW SLOW} [get_ports {LED8Bit[5]}]
# Bank: - GPIO_LED_6_LS
set_property -dict {PACKAGE_PIN E18 IOSTANDARD LVCMOS25 DRIVE 12 SLEW SLOW} [get_ports {LED8Bit[6]}]
# Bank: - GPIO_LED_7_LS
set_property -dict {PACKAGE_PIN F16 IOSTANDARD LVCMOS25 DRIVE 12 SLEW SLOW} [get_ports {LED8Bit[7]}]
# GPIO_DIP_SW0
set_property -dict {PACKAGE_PIN Y29 IOSTANDARD LVCMOS25 SLEW SLOW} [get_ports {DIPSw4Bit[0]}]
# GPIO_DIP_SW1
set_property -dict {PACKAGE_PIN W29 IOSTANDARD LVCMOS25 SLEW SLOW} [get_ports {DIPSw4Bit[1]}]
# GPIO_DIP_SW2
set_property -dict {PACKAGE_PIN AA28 IOSTANDARD LVCMOS25 SLEW SLOW} [get_ports {DIPSw4Bit[2]}]
# GPIO_DIP_SW3
set_property -dict {PACKAGE_PIN Y28 IOSTANDARD LVCMOS25 SLEW SLOW} [get_ports {DIPSw4Bit[3]}]
# GPIO_SW_N : SW2
set_property -dict {PACKAGE_PIN AA12 IOSTANDARD LVCMOS15 SLEW SLOW} [get_ports {BTN5Bit[0]}]
# GPIO_SW_E : SW3
set_property -dict {PACKAGE_PIN AG5 IOSTANDARD LVCMOS15 SLEW SLOW} [get_ports {BTN5Bit[1]}]
# GPIO_SW_S : SW4
set_property -dict {PACKAGE_PIN AB12 IOSTANDARD LVCMOS15 SLEW SLOW} [get_ports {BTN5Bit[2]}]
# GPIO_SW_C : SW5
set_property -dict {PACKAGE_PIN G12 IOSTANDARD LVCMOS25 SLEW SLOW} [get_ports {BTN5Bit[3]}]
# GPIO_SW_W : SW6
set_property -dict {PACKAGE_PIN AC6 IOSTANDARD LVCMOS15 SLEW SLOW} [get_ports {BTN5Bit[4]}]

#>-- LEDs, buttons and switches -->

#<-- UART --<

set_property -dict {PACKAGE_PIN K24 IOSTANDARD LVCMOS25} [get_ports {USB_RX}]
set_property -dict {PACKAGE_PIN M19 IOSTANDARD LVCMOS25} [get_ports {USB_TX}]

#>-- UART -->

#<-- control interface --<

set_false_path -from [get_pins -of_objects [get_cells -hierarchical -filter {NAME =~ *control_interface_inst*sConfigReg_reg[*]}] -filter {NAME =~ *C}]
set_false_path -from [get_pins -of_objects [get_cells -hierarchical -filter {NAME =~ *control_interface_inst*sPulseReg_reg[*]}] -filter {NAME =~ *C}]
set_false_path -to [get_pins -of_objects [get_cells -hierarchical -filter {NAME =~ *control_interface_inst*sRegOut_reg[*]}] -filter {NAME =~ *D}]

#>-- control interface -->

#<-- SMA MGT --<

set_property PACKAGE_PIN K2 [get_ports SMA_MGT_TX_P]
set_property PACKAGE_PIN K1 [get_ports SMA_MGT_TX_N]
set_property PACKAGE_PIN K6 [get_ports SMA_MGT_RX_P]
set_property PACKAGE_PIN K5 [get_ports SMA_MGT_RX_N]

# set_property LOC GTXE2_CHANNEL_X0Y8 [get_cells aurora_64b66b_inst/aurora_64b66b_0_support_inst/aurora_64b66b_0_i/inst/aurora_64b66b_0_wrapper_i/aurora_64b66b_0_multi_gt_i/aurora_64b66b_0_gtx_inst/gtxe2_i]
set_property LOC GTXE2_COMMON_X0Y2 [get_cells aurora_64b66b_inst/aurora_64b66b_0_support_inst/gt_common_support/gtxe2_common_i]

#>-- SMA MGT -->

#<-- ten gig eth interface --<

# SFP
set_property -dict {PACKAGE_PIN Y20 IOSTANDARD LVCMOS25} [get_ports SFP_TX_DISABLE_N]
set_property -dict {PACKAGE_PIN P19 IOSTANDARD LVCMOS25} [get_ports SFP_LOS_LS]
set_property PACKAGE_PIN H2 [get_ports SFP_TX_P]
set_property PACKAGE_PIN H1 [get_ports SFP_TX_N]
set_property PACKAGE_PIN G4 [get_ports SFP_RX_P]
set_property PACKAGE_PIN G3 [get_ports SFP_RX_N]

# False paths for async reset removal synchronizers
set_false_path -to [get_pins -of_objects [get_cells -hierarchical -filter {NAME =~ *ten_gig_eth_pcs_pma_core_support_layer_i/*shared*sync1_r_reg*}] -filter {NAME =~ *PRE}]
set_false_path -to [get_pins -of_objects [get_cells -hierarchical -filter {NAME =~ *ten_gig_eth_pcs_pma_core_support_layer_i/*shared*sync1_r_reg*}] -filter {NAME =~ *CLR}]

# Constraint for GT location
#set_property LOC GTXE2_CHANNEL_X0Y10 [get_cells ten_gig_eth_pcs_pma_core_support_layer_i/ten_gig_eth_pcs_pma_i/*/gt0_gtwizard_10gbaser_multi_gt_i/gt0_gtwizard_10gbaser_i/gtxe2_i]
set_property LOC GTXE2_COMMON_X0Y2 [get_cells ten_gig_eth_cores.ten_gig_eth_inst/ten_gig_eth_pcs_pma_inst/ten_gig_eth_pcs_pma_core_support_layer_i/ten_gig_eth_pcs_pma_gt_common_block/gtxe2_common_0_i]

# create_generated_clock -name ddrclock -divide_by 1 -invert -source [get_pins *rx_clk_ddr/C] [get_ports xgmii_rx_clk]
# set_output_delay -max 1.500 -clock [get_clocks ddrclock] [get_ports * -filter {NAME =~ *xgmii_rxd*}]
# set_output_delay -min -1.500 -clock [get_clocks ddrclock] [get_ports * -filter {NAME =~ *xgmii_rxd*}]
# set_output_delay -max 1.500 -clock [get_clocks ddrclock] [get_ports * -filter {NAME =~ *xgmii_rxc*}]
# set_output_delay -min -1.500 -clock [get_clocks ddrclock] [get_ports * -filter {NAME =~ *xgmii_rxc*}]

#>-- ten gig eth interface -->

#<-- gigabit eth interface --<

set_property -dict {PACKAGE_PIN L20 IOSTANDARD LVCMOS25} [get_ports PHY_RESET_N]
set_property -dict {PACKAGE_PIN J21 IOSTANDARD LVCMOS25} [get_ports MDIO]
set_property -dict {PACKAGE_PIN R23 IOSTANDARD LVCMOS25} [get_ports MDC]
#
set_property -dict {PACKAGE_PIN U28 IOSTANDARD LVCMOS25} [get_ports RGMII_RXD[3]]
set_property -dict {PACKAGE_PIN T25 IOSTANDARD LVCMOS25} [get_ports RGMII_RXD[2]]
set_property -dict {PACKAGE_PIN U25 IOSTANDARD LVCMOS25} [get_ports RGMII_RXD[1]]
set_property -dict {PACKAGE_PIN U30 IOSTANDARD LVCMOS25} [get_ports RGMII_RXD[0]]
set_property -dict {PACKAGE_PIN L28 IOSTANDARD LVCMOS25} [get_ports RGMII_TXD[3]]
set_property -dict {PACKAGE_PIN M29 IOSTANDARD LVCMOS25} [get_ports RGMII_TXD[2]]
set_property -dict {PACKAGE_PIN N25 IOSTANDARD LVCMOS25} [get_ports RGMII_TXD[1]]
set_property -dict {PACKAGE_PIN N27 IOSTANDARD LVCMOS25} [get_ports RGMII_TXD[0]]
set_property -dict {PACKAGE_PIN M27 IOSTANDARD LVCMOS25} [get_ports RGMII_TX_CTL]
set_property -dict {PACKAGE_PIN K30 IOSTANDARD LVCMOS25} [get_ports RGMII_TXC]
set_property -dict {PACKAGE_PIN R28 IOSTANDARD LVCMOS25} [get_ports RGMII_RX_CTL]
set_property -dict {PACKAGE_PIN U27 IOSTANDARD LVCMOS25} [get_ports RGMII_RXC]

# already set in ip / tri_mode_ethernet_mac_0.xdc
# create_clock -period 8 [get_ports RGMII_RXC]
set rx_clk_var [get_clocks -of [get_ports RGMII_RXC]]
set_clock_groups -asynchronous -group [get_clocks -include_generated_clocks -of_objects [get_ports RGMII_RXC]] -group [get_clocks -include_generated_clocks sgmii_clock]

set_property IODELAY_GROUP tri_mode_ethernet_mac_iodelay_grp [get_cells -hier -filter {name =~ *trimac_fifo_block/trimac_sup_block/tri_mode_ethernet_mac_idelayctrl_common_i}]
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

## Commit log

2017-03-28 Initial KiCad script and example project
    [Phi10cmBonding.kicad_pcb, Phi10cmBonding.sch]
2017-04-05 First example of correct net handling and zone filling
    [Phi10cmBonding.kicad_pcb, Phi10cmBonding.sch, template.kicad_pcb]
2017-04-10 Add Topmetal-S schematic symbol lib and KiSch class to add it.
    [Phi10cmBonding.sch]
2017-04-11 Add KiPcbFp footprint generation
    [Phi10cmBonding.sch]
2017-04-13 Create a reasonable unit cell.
    [TMS1mm1chip.kicad_pcb, TMS1mm1chip.sch]
2017-04-17 Achieve reasonable array generation.
    [Phi10cmBonding.kicad_pcb, Phi10cmBonding.sch, TMS1mm1chip.kicad_pcb, TMS1mm1chip.sch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]
2017-04-21 Add FSI-150-XX-X-D-X-XX connector symbol and footprint
    [Phi10cmBonding.sch, array.sch, connector.sch]
2017-04-25 Add FSI-150-XX-X-D-X-AD-solder-Front and a FPGA carrier board sketch
    [carrier.kicad_pcb]
2017-04-28 Update SNx5LVDx386 and FSI footprint
    [carrier.sch]
2017-05-31 First array of 19 using 2 external DACs per sensor.
    [TMS1mm1chip.kicad_pcb, TMS1mm1chip.sch, TMS1mm2ExDACx19.sch, carrier.kicad_pcb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]
2017-07-15 First array of 19 with Aout1or2
    [TMS1mm1chip.kicad_pcb, TMS1mm1chip.sch, TMS1mmX19.sch, connector.sch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]
2017-08-03 First production-ready PCB/TMS1mmX19
    [TMS1mm1chip.kicad_pcb, TMS1mmX19.kicad_pcb, TMS1mmX19.sch, array.sch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]
2017-08-10 TMS1mmX19Carrier work-in-progress
    [TMS1mmX19Carrier.sch]
2017-08-12 TMS1mmX19Carrier first version sent out for PADS layout.
    [TMS1mmX19Carrier.sch]
2017-08-13 Update CSA_EXT CON and power CON before sending out for PADS layout.
    [TMS1mmX19Carrier.sch]
2017-08-17 Corrected the hole locations, SM1~4, for TE0741.
2017-10-08 Lower aurora_64b66b line rate to 3.125Gbps Files under src/aurora64b66b/ for the two devices are identical but are kept as separate copies. Reformat .xdc using set_property -dict
2017-11-10 Implement sensor working mode selection through argparse.
    Add socket.MSG_WAITALL into recv() calls.
    Reduce wait in tms_sio_rw().
    Add SDM data demux and data saving to files.
